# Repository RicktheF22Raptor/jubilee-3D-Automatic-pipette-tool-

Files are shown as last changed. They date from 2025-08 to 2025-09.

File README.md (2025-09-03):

This tool is based primaraly on the work described in the article "How to convert a 3D printer to a personal automated liquid handler for life science workflows" in this paper 
they describe the modifications needed in order to convert an Ender 3 3D printer into a platform for automating liquid handling for the purposes of autmating expiermentation 
as well as more generally democratizing self running lab technology.The purpose behind the tool I designed is to further expand access to the same liquid handeling capablity on a morerobust platfrom like the Jubilee 3D, this is is meant to act as an inexpensive alternative to other liquid handeling tools currently available publically on the Jubilee, without requiring new users to modify the tool themselves, the Jubilee spefically is a far more robust movement platform whose prepratary software is purpose built for utilizing a varity of tools which makes the proccess of adding the liquid handeling tool much smoother compared to what can be the fickel proccess of modify the ender.

References:

-Naranbat, D., Phelps, B., Murphy, J., & Tripathi, A. (2025). How to convert a 3D printer to a personal automated liquid handler for life science workflows. SLAS Technology, 30, 100239. https://doi.org/10.1016/j.slast.2024.100239 

-🔬🧪 science jubilee ⚡⚙️#. 🔬🧪 Science Jubilee ⚡⚙️ - Science Jubilee 0.3.2.post1.dev200+gdd7e0ef documentation. (n.d.). https://science-jubilee.readthedocs.io/en/latest/index.html 

# jubilee-3D-Automatic-pipette-tool-
Find here all the necessary resources to build a Pipetting tool for the Jubilee 3D

All necessary components:

# Parts — not included in Jubilee "vitamin kit"

| Quantity | Part / Type                                                          | Notes / Link |
|----------|-----------------------------------------------------------------------|--------------|
| 1x       | Each 3D printed part                                                  | (printed on-demand / repo) |
| 1x       | Captive linear stepper motor (25 mm can-stack captive stepper)        | [Haydon Kerk Pittman product page](https://www.haydonkerkpittman.com/products/linear-actuators/can-stack-stepper/25mm-25000) |
| 1x       | E1 ClipTip — Tip Cone Assembly, Plastic Tip Fitting, single channel, 125 µL | [PipetteSupplies product](https://www.pipettesupplies.com/product/e1-clip-tip-tip-cone-assembly-plastic-tip-fitting-single-channel-125μl-thermo-scientific/) |
| 2x       | M3 button-head screw, **8 mm** long                                   | (not provided in vitamin kit) |
| 2x       | 2-64 × 0.4375" flathead screw                                         | (thread & length per original list) |
| 1x       | SS-5GL limit switch (Omron SS-5GL snap/limit switch)                  |(https://www.digikey.com/en/products/detail/omron-electronics-inc-emc-div/SS-5GL/272367) · 
| 1x       | Jubilee / Generic Extra Tool — "Vitamin kit"                          | (https://www.lukeslabonline.com/products/jubilee-generic-extra-tool-vitamin-kit?srsltid=AfmBOopn3gWTzfLxL6CEZkIZTFIs6pjnynb042KZSuh6t3ffAsHF3te0)

# Jubilee / Generic Extra Tool — "Vitamin kit" (contents)

_Kit product page: Luke’s Lab Online — Jubilee/Generic Extra Tool Vitamins Kit.

| Qty | Item description (as listed on Luke's Lab)         |
|-----:|---------------------------------------------------|
| 2   | M5×60 dowel rod                                   |
| 6   | M3×6 button-head screw                            |
| 4   | M3×10 button-head screw                           |
| 2   | M3×12 button-head screw                           |
| 3   | M3×40 button-head screw                           |
| 6   | M3×8 flathead screw                               |
| 11  | M3×6 flathead screw                               |
| 6   | M5×10 button-head screw                           |
| 9   | M3 heat tapered inserts (heat-set inserts)        |
| 6   | M5 hammer nut                                     |
| 1   | Wiper                                             |
| 3   | M3 threaded 8 mm balls (tool balls)               |
| 2   | O-rings (pair)                                    |
| 1   | Wedge plate                                       |

# Basic assembly instructions:

1.Screw in stainless steel balls with 8mm M3 screws 

2.Use a soldering iron to set the heat set inserts on into the holes for the motor as well as the tool wedge holes. Also set in the heat insert into limit switch trigger 

3.Screw in tool wedge with M3 Screws flat head 8mm long

4.Screw limit switch on the end of the captive motor 

5.Screw in limit switch with 2-64 screws

6.Place tip cone assembly plunger into limit switch 

7.Assemble rest of the tip cone assembly and screw into tool body insuring spring stays in the section with the threading along with both O rings

8.Screw in the motor and make sure the limit switch trigger fits into the slot along the side.

9.-Done

# wiring set up 

1.Each wire is extended approxiamtely 150mm in order to ensure it can comforably operate around the Jubilee 

2.At the end of the wires we will crimp on a Female JST XH 6 pin connecter in this order with the connecter side you are onable to see the crimps through facing away from you 

a. Red to the farthest right port

b. Black to the middle closet to red(skip one port) 

c. Green to the farthest left port

d. Blue to the middle directly next to Black



# Automatic Tip ejection:

For any expirment that requires replacing the tips mid operation, we have designed an attachement to the lab automation plate to automaticly
eject tips, the deisgn is based on the same principle as the Naranbat design, and the tip is meant to go inside the basket before jogging over to the head and having 
the head pull down on the spring loaded cone assembly thereby ejecting the tip.

File Name(s): Tip ejction basket and Tip Ejctor Head

Instructions: Assume you are facing the Jubilee with the Y railing point parrallel to where you'r eyes are pointing, and the tool holder facing to your left. 

1.Print both pieces and attach the head to the body using 2 6-32 8mm* long countersink screws 

2.dettach the bed plate L bracket closest to the left corner

3.Using the same M3 screws as the L bracket, screw in the Basket assembly until firmly in place(a little wobble is ok as long as the face the screws go into is flat against the plate) 

4. Create a Macro on the Jubilee and copy this g code script(positions are not exact and you should adjust these to your liking or necessity)
     G90 ;set absolute positioning

     G1 Z185 ;move bed to allow pippette tip to clear all objects on lab plate

     G1 X207 ;moves the pipette within the area of the basket but clear of the ejctor head
     G1 Y280

     G1 Z80 ;moves the bed up so the Ejector head is at the same height as the cone assembly neck

     G1 X287 ;places the ejector head around the neck of the Cone assembly 

     G1 Z90 ; moves ejctor up and then down to eject the tip
     G1 Z80

     G1 X207 ; moves the Pipette away from the ejector neck

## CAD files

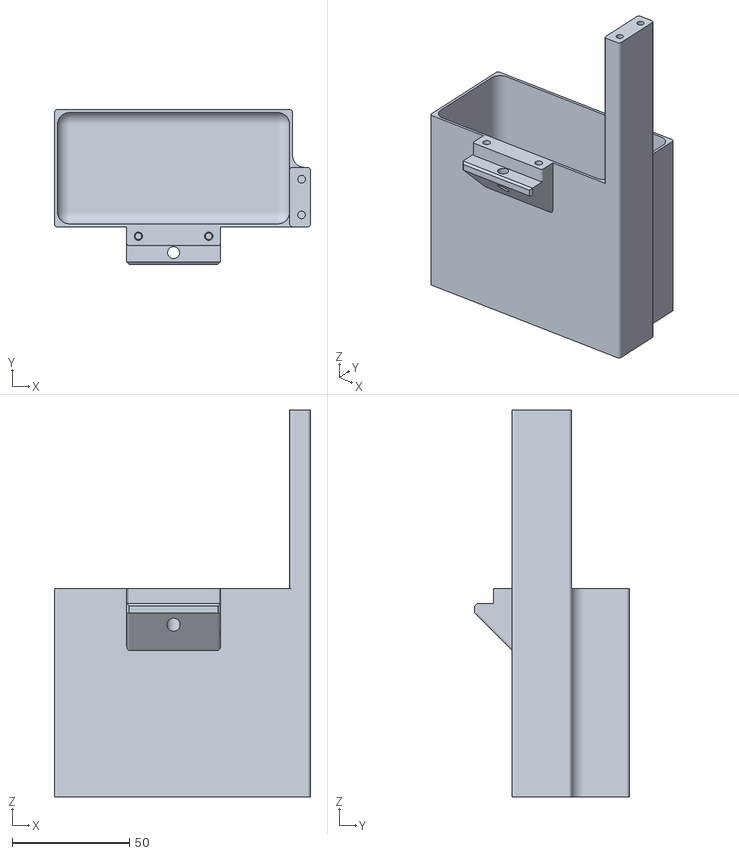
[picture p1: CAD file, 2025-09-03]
Tip Ejection basket.stl
109.2 x 66.0 x 165.1

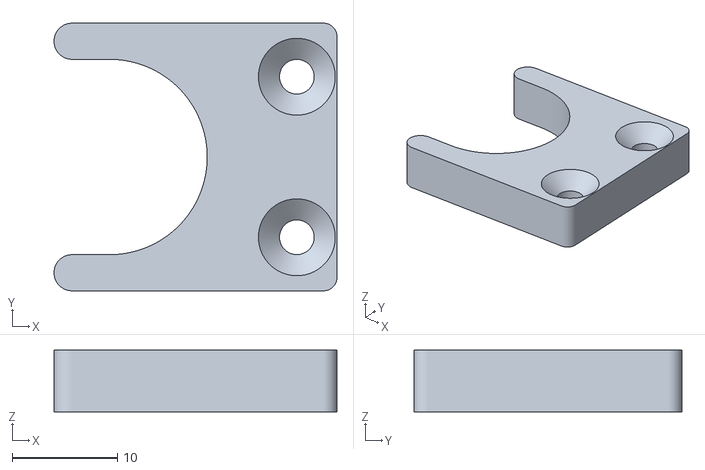
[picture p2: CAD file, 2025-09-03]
Tip Ejector Head.stl
26.9 x 25.4 x 5.84

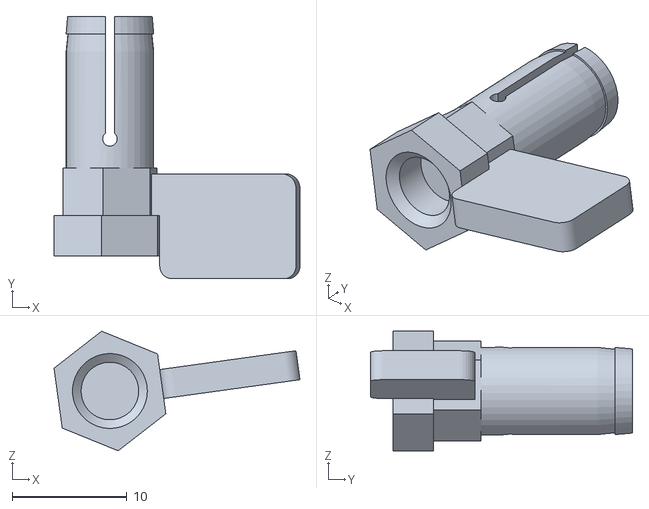
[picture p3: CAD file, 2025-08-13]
Limit switch trigger updated 2.stl
21.4 x 22.8 x 10.4

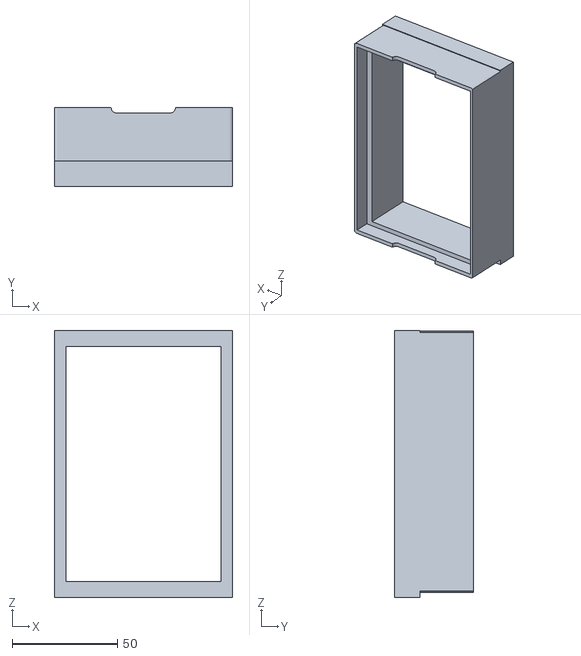
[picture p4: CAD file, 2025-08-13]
Pipette tip holder.stl
84.5 x 37.3 x 126.7

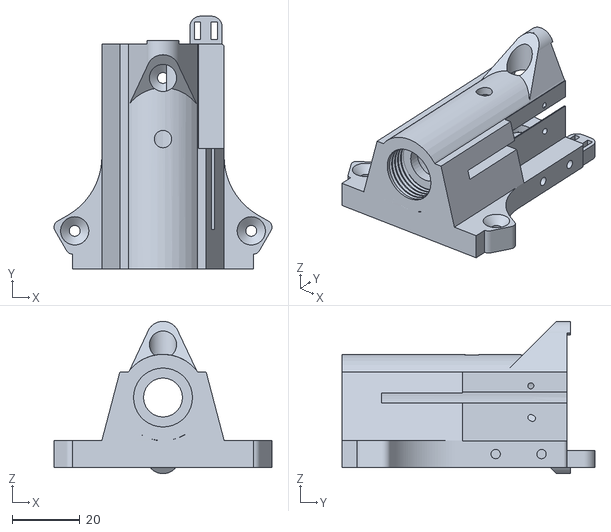
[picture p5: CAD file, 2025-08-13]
Pipette holder updated 3.stl
64.2 x 74.3 x 44.8

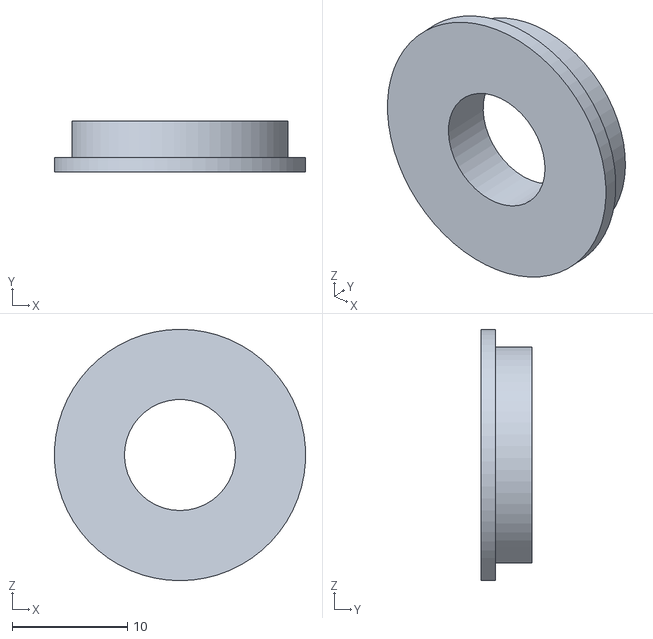
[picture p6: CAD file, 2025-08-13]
B_pipette_cone_head.STL
21.8 x 4.45 x 21.8

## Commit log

2026-04-12 Rename Pipette tip holder.stl to Parts/Pipette tip holder.stl
2026-04-12 Rename Pipette holder updated 3.stl to Parts/Pipette holder updated 3.stl
